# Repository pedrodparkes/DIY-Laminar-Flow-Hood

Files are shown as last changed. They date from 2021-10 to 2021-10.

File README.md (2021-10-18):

# Практическое руководство по сборке ламинарного бокса

<br/>

Данное руководство представлено для тех, кто ознакомлен с альтернативными способами снижения уровня контаминации, решил, что ламинарный бокс ему точно необходим, и готов инвестировать в оборудование. <b>Руководство неидеально (v.0.1), может содержать ошибки и, как и его читатель, будет совершенствоваться.</b>

\* Само по себе <b>Обладание ламинарным боксом</b> не гарантирует решение всех проблем и снижение уровня контаминации.

<br/><br/>

## <b>1. Рассчет мощности вентилятора</b>

[Рассчитываем мощность радиального вентилятора, в соответствии с сопротивлением предфильтра и HEPA-фильтра](https://youtu.be/MmqCsO1DsY0?t=365)

\* В дальнейшем тут будет подробное описание рассчетов

<br/><br/>
## <b>2. Закупка комплектующих</b>

| №  | Наименование  | Характеристики | UA | RF | EMEA | USA |
|---|---|---|---|---|---|---|
| 1 | HEPA-фильтр  | 1000х600мм  |   |   |   |   |
| 2 | Вентилятор   |   | [Купить](https://turbovent.com.ua/p1130397844-ventilyator-radialnyj-turbovent.html)  |   |   |   |
| 3 | Фанера  | Толщина 15мм  | [Купить](https://epicentrk.ua/ua/shop/fanera-fk-vlagostoykaya-1250x2500x15-mm-sort-3-4.html)  |   |   |   |
| 4 | Саморезы по дереву  | Длина 30мм  | [Купить](https://epicentrk.ua/ua/shop/samorez-po-derevu-potay-3x30-mm-200-sht-stal-chernyy-amig.html)  |   |   |   |

<br/><br/>
## <b>3. Спецификации компонентов</b>

## <b>3.1 HEPA-фильтр </b>

<b>[Паспорт HEPA](docs/Laminar_details.pdf)

<br/><br/>

## <b> 3.2 Вентилятор </b>

|   |  |  |
|---|---|---|
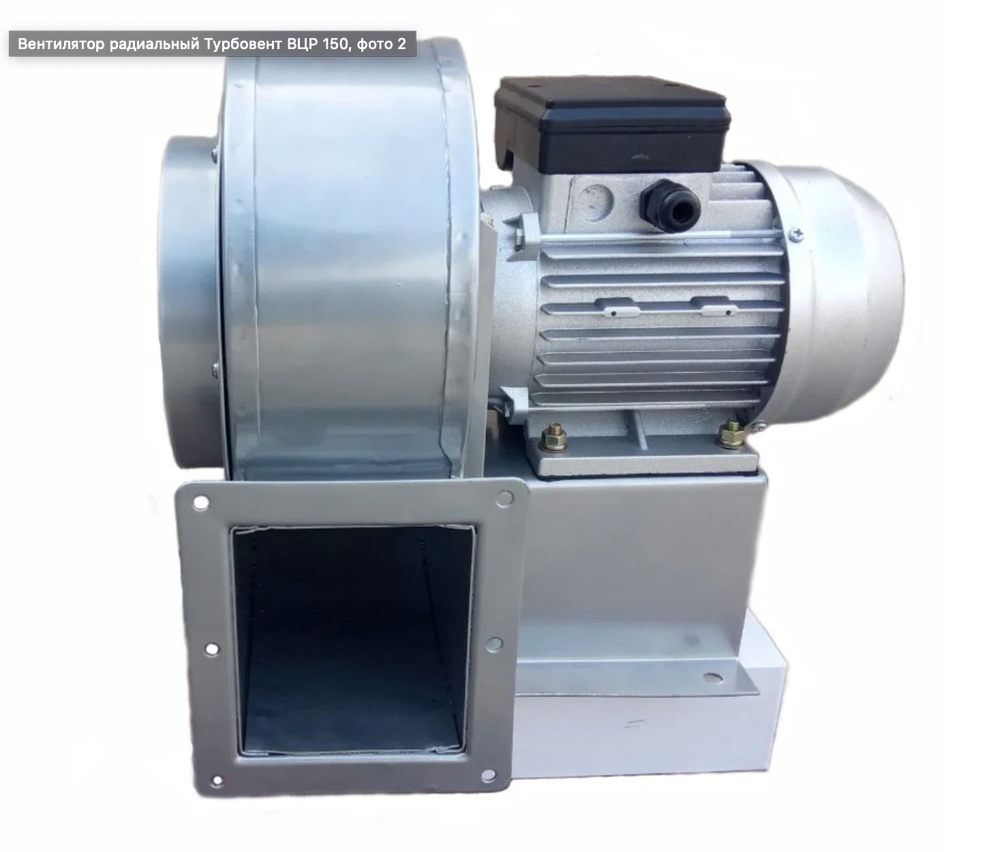
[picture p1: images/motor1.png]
m1
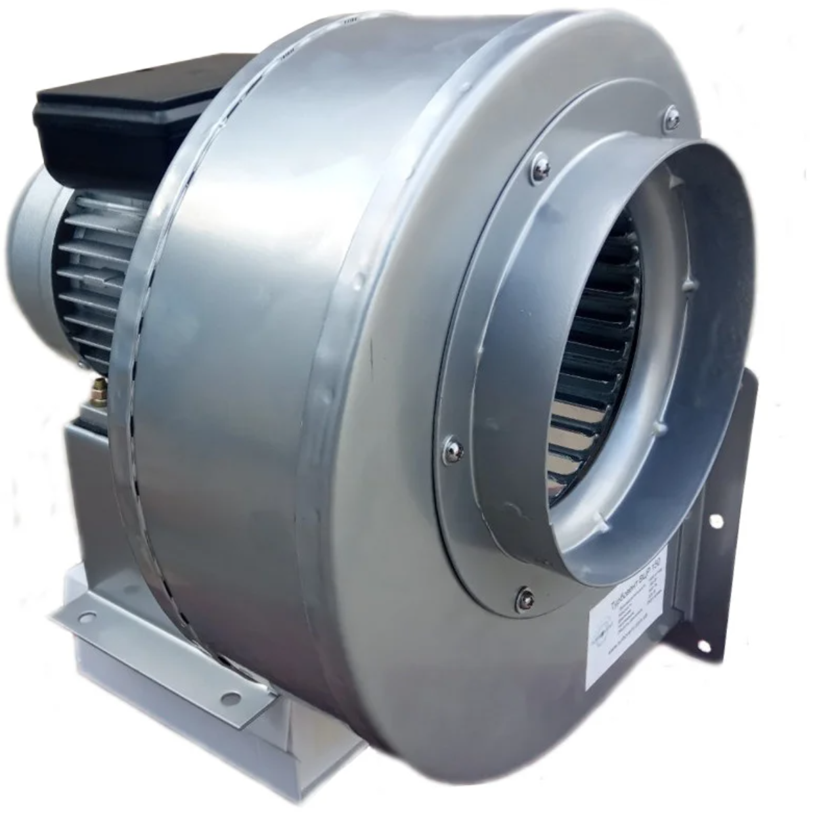
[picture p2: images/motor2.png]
m2
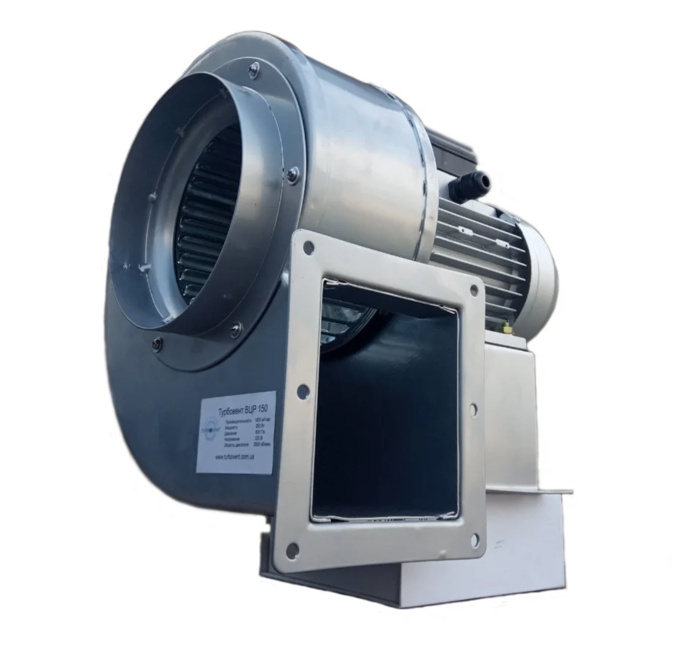
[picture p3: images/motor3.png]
m3
|   |   |  |

<br/>

### <b>Характеристики вентилятора </b>

|   |   |
|---|---|
|Расход воздуха  	|1900 куб. м/час|
|Скорость вращения	|2800 об/мин|
|Потребляемая мощность  	|250 Вт|
|Напряжение сети  	|220~240 В|
|Вес	|10 кг|
|Материал корпуса	|Сталь|
|Высота	|350 мм|
|Ширина	|355 мм|
|Глубина	|330 мм|
|Требуемый диаметр воздуховода	|150 мм Подробнее: https://turbovent.com.ua/p1130397844-ventilyator-radialnyj-turbovent.html|

<br/>

<br/>

### <b>Чертеж вентилятора </b> (инвертированный по Y (вертикали), то есть мотор находится над, а не под выходом воздуховода)
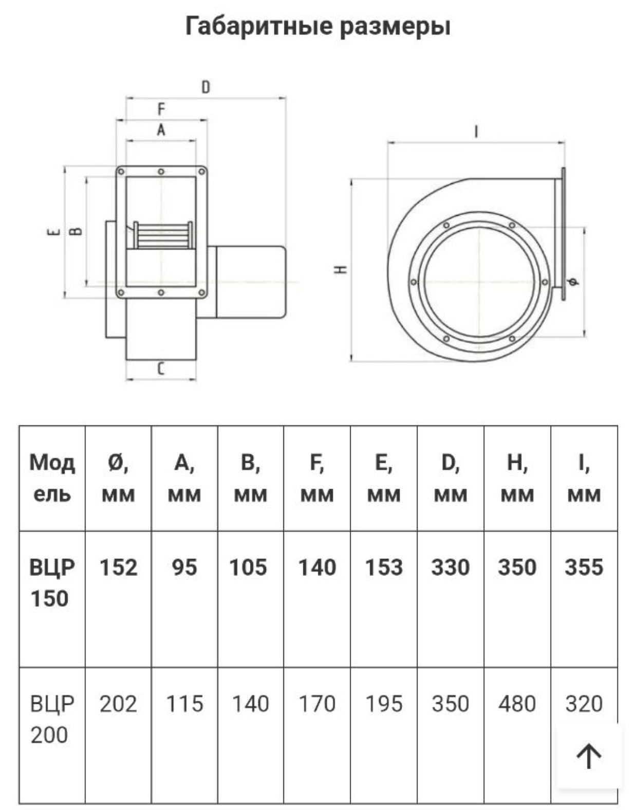
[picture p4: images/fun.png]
Чертеж вентилятора


<br/><br/>

## <b>4. Изготовление необходимых детали из фанеры</b>
<br/>

### Устройство состоит из двух боксов. Ламинарного и предфильтра.

    Материал - фанера 15мм
### Распил удобнее произвести у продавца материала по предоставленной ниже спецификации

| №: |  Деталь | Размеры, мм  | Количество, шт  |
|---|---|---|---|
|1 | Основание ламинарного бокса | 1030х515 | 1  |
|2 | Боковые панели ламинарного бокса  | 630х500  | 2  |
|3 | Задняя крышка ламинарного бокса  | 1030х630  | 1  |
|4 | Ребра жесткости ламинарного бокса (установлены за хепа-фильтром)  | 1000x30  | 2  |
|5 | Верхняя крышка ламинарного бокса  | 1000х500   | 1   |
|6 | Отверстие верхней крышки  | 105х95  | 1 |
|7 | Расстояние от отверстия верхней крышки до задней стенки  | 72.6мм  | n/a  |
|8 | Прокладка под вентилятор из резины толщиной 2мм  | 140х153 | 1  |
|9 | Отверстие в прокладке под вентилятор  | 105х95  | 1  |
|10| Передняя и задняя стенки предфильтра  | 543.9x450  | 2   |
|11| Боковые стенки  предфильтра  | 458x450 | 2  |
|12| Верхняя крышка предфильтра  | 544х487.6 | 1  |

<br/><br/><br/>
## <b>5. Сборка:</b>

<br>

<b>5.1 Все детали отшлифовать орбитальной шлиф-машиной шкурой 100-400 грип</b>

<br/>

<b>5.2 Все детали промазать масло-воском со всех сторон и дать высохнуть. (если не принято решение красить)

<br/>

<b>5.3 Собрать короб ламинарного бокса на саморезы, вкрученные в торец (перед вкручиванием саморезов, отверстия засверлить сверлом меньшего диаметра, чтобы предотвратить растрескивание фанеры)

<br/>

<b>5.4 Убедиться, что хепа-фильтр становится в посадочное место

<br/>

<b>5.5 Выставить хепа-фильтр по-глубине в коробе. Сзади него прикрутить два ребра жесткости

<br/>

<b>5.6 Предфильтр отложить в сторону, чтоб не забился пылью от работы

<br/>

<b>5.7 Убедиться, что вентилятор становится на указанное место.

<br/>

<b>5.8 Вырезаnm в верхней панели отверстие для установки вентилятора

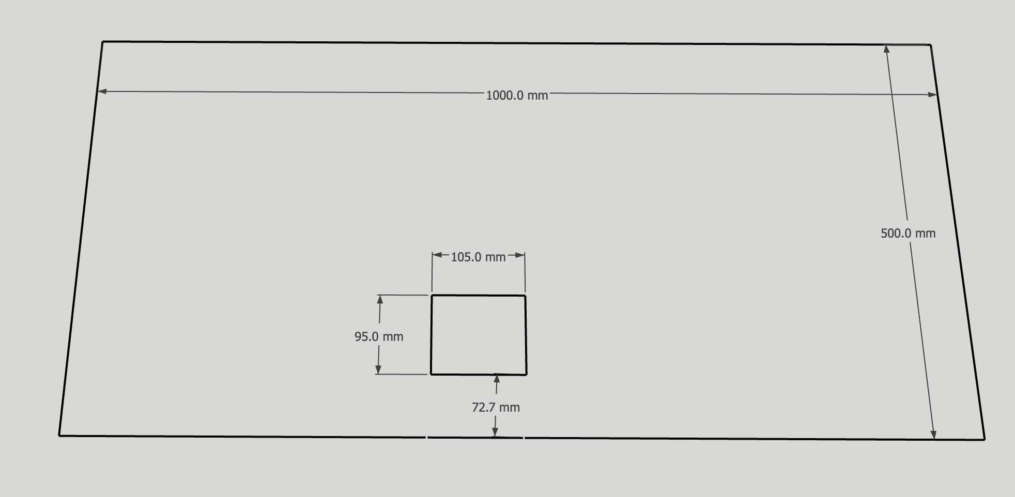
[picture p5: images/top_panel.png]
Верхняя панель


<br/>

<b>5.9 Вырезать из резины толщиной 2мм прямоугольник с отверстием, который послужит демпфером крепления вернтилятора. 
    
    Внешний размеры: 153х140
    Внутренний размер (отверстия): 105х95
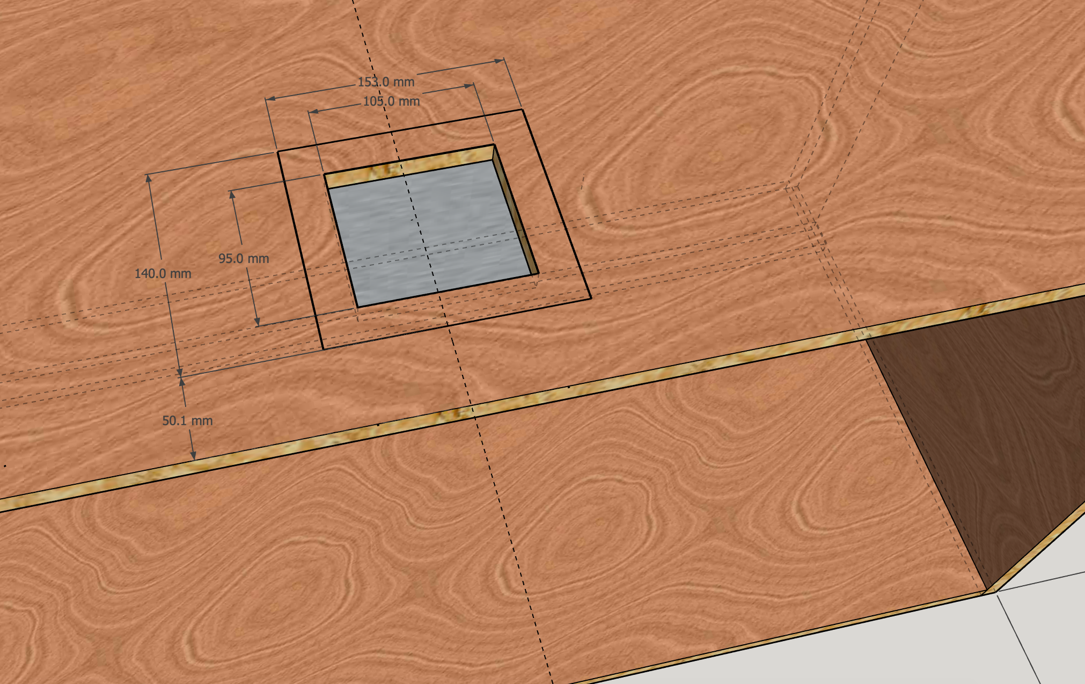
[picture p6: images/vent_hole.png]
Отверстие установки вентилятора


<br/>

<b>5.10 Приклеиваем эластичным клеем демпферную резинку к корпусу ламинарного бокса.

<br/>

<b>5.11 Устанавливаем части короба предфильтра:</b>
    
    Боковые панели: 457.6x450
    Задняя и передняя панели: 543.9х450

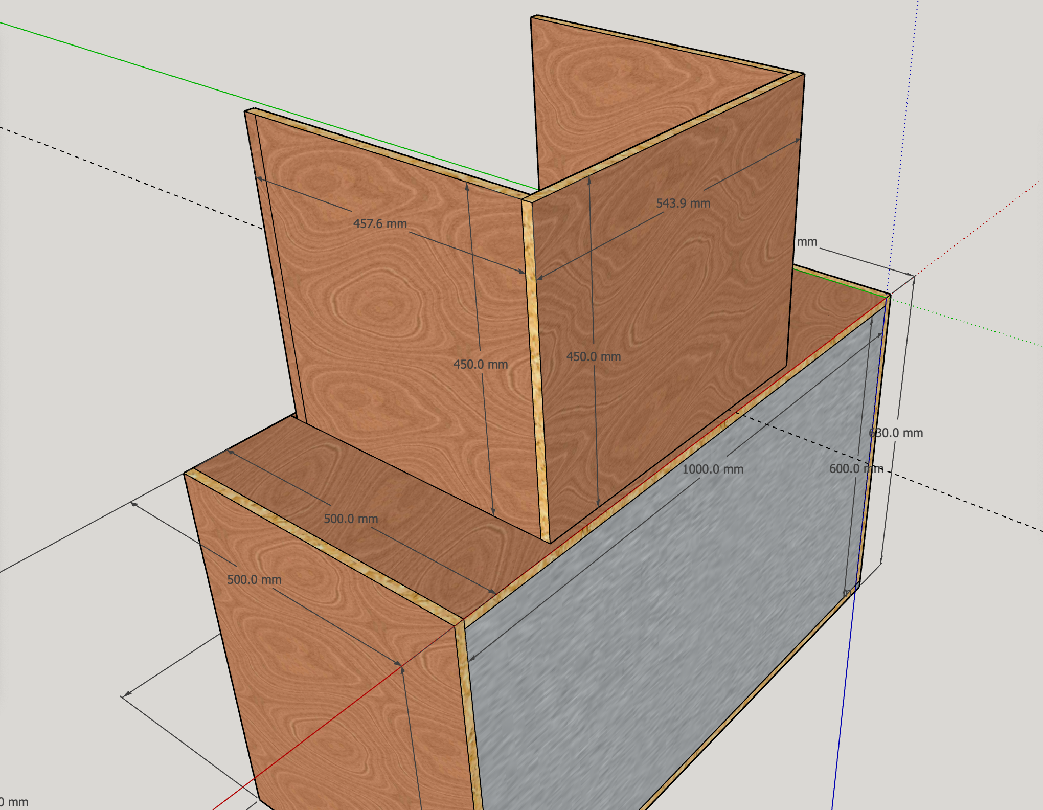
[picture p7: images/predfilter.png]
короб предфильтра


<br/>

<b>5.12 Красим все части снаружи и изнутри (если не было принято решение пропитывать масло-воском).

<br/>

<b>5.13 Устанавливаем вентилятор:
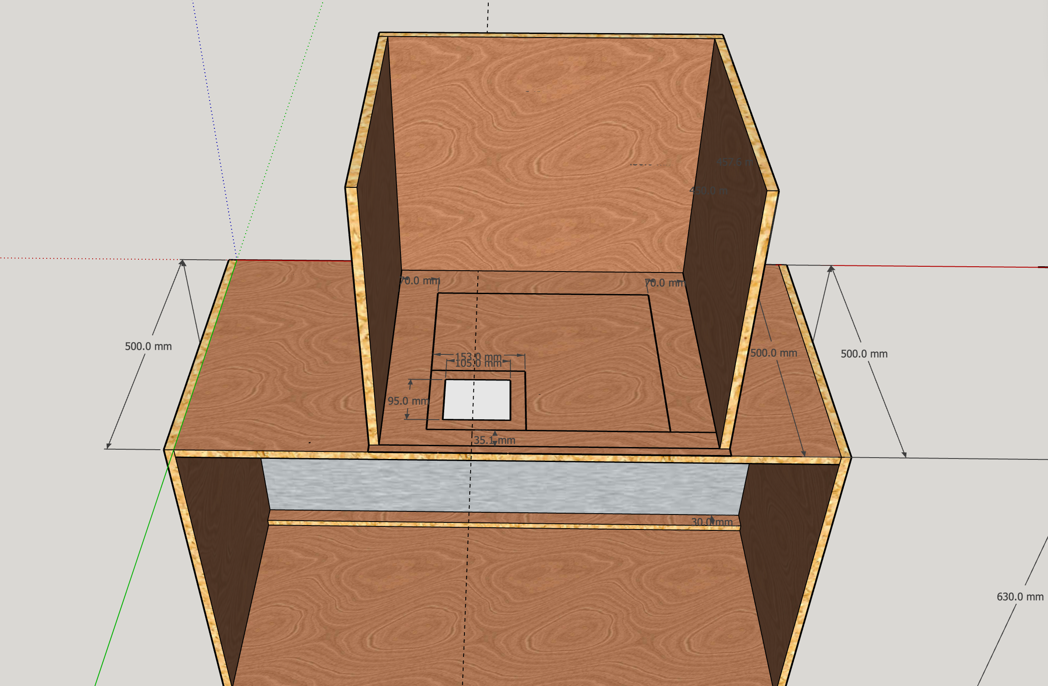
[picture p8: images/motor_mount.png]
Устанавливаем мотор


<br/>

<b>5.14 Устанавливаем заднюю крышку мотора
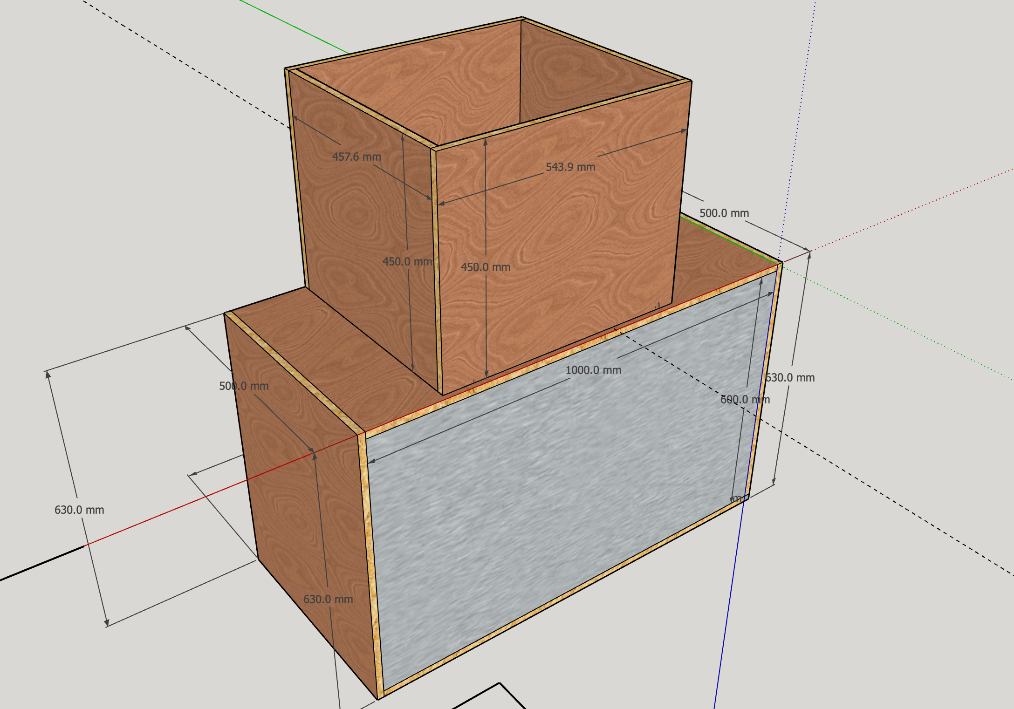
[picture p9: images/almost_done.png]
Задняя крышка мотора


<br/>

<b>5.15 Устанавливаем верхнюю крышку предфильтра:

    Размеры: 543.9x487.6
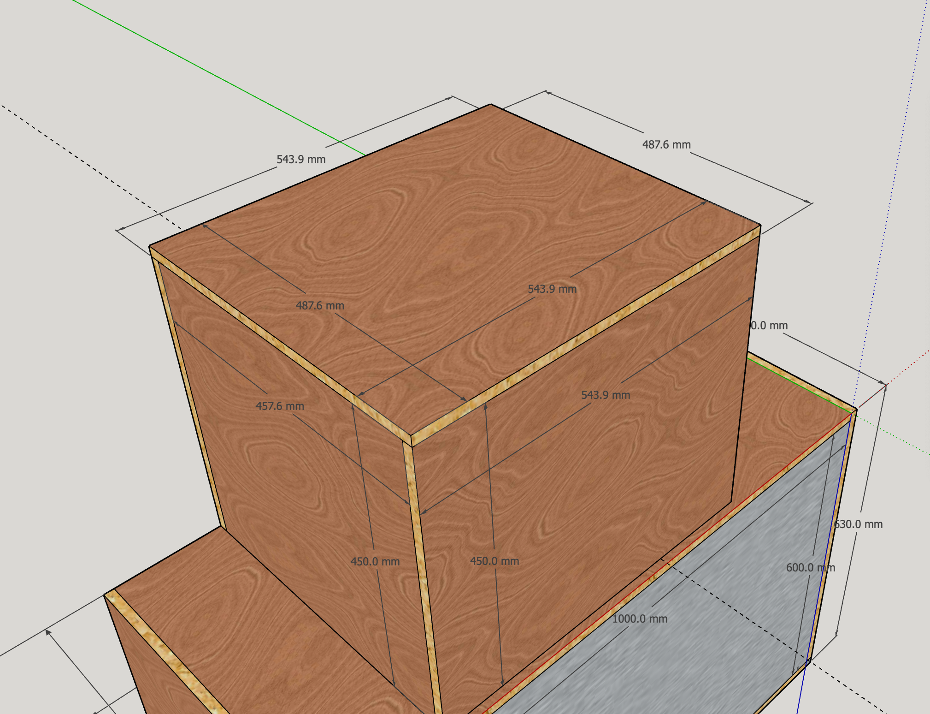
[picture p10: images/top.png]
Верхняя кышка предфильтра


<br/>

<b>5.16 Сверлим отверстие для кабеля питания, соединяем провода, устанавливаем тумблер вкл/выкл (с таймером выключения, по желанию)

<br/>

<b>5.17 Устанавливаем заднюю крышку ламинарного бокса:

        Размеры: 1030х630

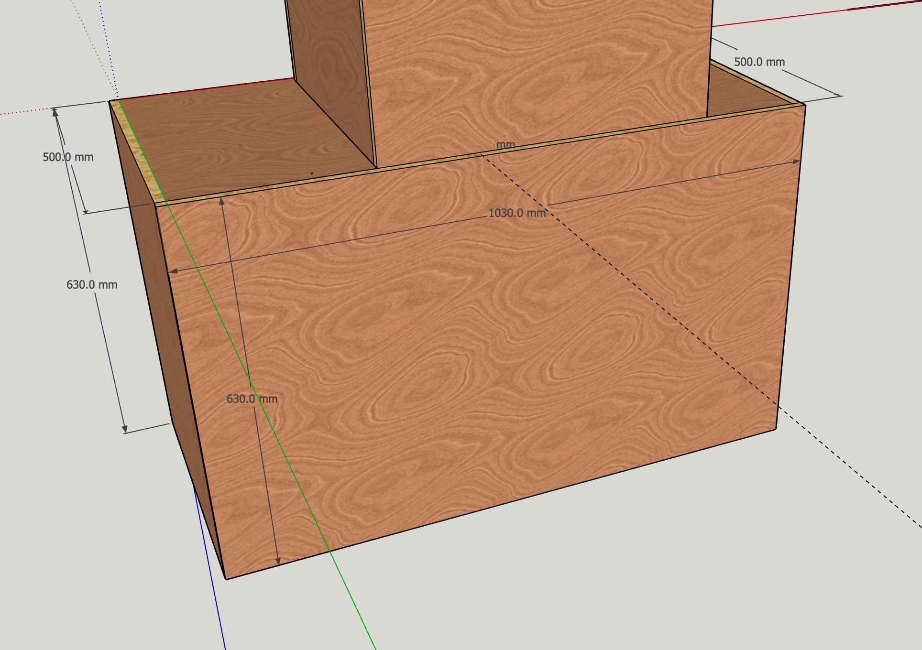
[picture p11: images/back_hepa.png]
Задняя крышка


<br/>

<b>5.18 Устанавливаем хепа-фильтр. Используя доступный уплотнитель, проклеиваем щели за хепа-фильтром

<br/>

<b>5.19 Устанавливаем заднюю крышку ламинарного бокса

<br/>

<b>5.20 Вы достигли пункта 4-20 и стали обладателем новенького ламинарного бокса. Ура!

<br><br>

\* Если вы встретили ошибку в данном руководстве, хотите предложить свой вариант чертежа, способ удешевления или улучшения конструкции,  гайд эксплуатации - дайте мне знать.

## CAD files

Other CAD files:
Laminar.skp
